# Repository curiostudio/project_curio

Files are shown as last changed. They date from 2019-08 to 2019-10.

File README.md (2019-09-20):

# An open source Human Computer Interface to help Blind users to code
 
I am working on this project for my thesis in Integrated Product Design, and I wanted to make this project open source, so as widen its
impact and ensure it reaches the last mile. As a product designer and mechanical engineer by background, I believe I am limited. This is
is an effort to explore and introduce a new approach towards bringing more blind users into the programming world. I believe, only with community development, can this project reach its fullest potential. Hence, I invite designers, engineers, computer scientists and enthusiasts to make the world of programming accessible for all. 

# The Story
I am an Integrated Product Design  student of the Industrial Design Faculty at the Delft University of Technology. My thesis is on 
'Development of a HCI device to enable blind children to learn coding'. In the 21st century, learning to code is synonymous and as 
important as learning a new language. Lack of Computational Thinking (CT), which coding helps to develop, results in blind users missing on
Lucrative jobs in the programming world. for blind people. Visually impaired people have a hard time finding job opportunities. Finding one requires their workplace
and their travel to the workplace are accessible too. On the other hand, blind people can work from home when it comes to programming jobs.
Moreover, the popular assistive tools like Refreshable Braille Displays, though inaccessible (by purchasing power) to most users,
are the 'only' available option in the market to help blind people to code. There are four major problems that prevents the majority
users in this target group to learn and use coding- 

 1) The global braille literacy is very low, meaning most of them depend on screen readers as they cannot use braille based assistive 
    aids like the Braille displays. According to the European Blind Union, braille illiteracy causes 75% of their unemployability scenarios.

 2) Refreshable braille displays are expensive, for individuals in the middle and low income groups to afford. During my research in 
    India, I found that only a  few (even) blind schools knew about these braille displays and that too they have seen only in the 
    magazines/ websites. It is simply too expensive to own one. 

 3) Screen readers (that is available for free) is designed to read only natural language and not source code. Though these softwares can be 
    configured to read symbols or to skip them, it is often difficult to say which configuration would best suited to understand the 
    code in consideration, and 

 4) Use of these aids, greatly reduces the productivity and ability collaborate (in professional environments) and ability to learn 
    from peers(in school environments)

 # Some background research

In the past two decades, several educational materials have been developed for children to learn digital skills like LEGO Mindstorms, 
BBC Micro:bit, online games and puzzles. Most programming languages for children are block based, meaning they arrange virtual blocks on
the screen to form a logical pattern. The debugging is also presented with visual cues . The output is also in the form of visual- 
animations and digital games. However these materials are not accessible to visually impaired children.  Programming languages for
children and teens are mostly block based, like SCRATCH and BLOCKLY. An Interview with the ICT teacher at a Visio, an umbrella 
organisation for blind schools  in the Netherlands,  revealed that the common medium of insruction for high school blind students 
is Python language. Studies by McKay and Kolling, 2013 explains that block languages are suited to deletion and movement, while 
textual language are suited for some other tasks like insertion and replacement. Owing to the fact that the project aims at gearing up
students to suit the employment market better, a textual programming language in python was chosen as the starting point. 

As the ICT world is becoming increasingly accessible to users with disabilities including blindness, languages like Quorum have been
developed in recent years. It is the world’s first evidence based programming language developed upon the SodBeans environment. 
Although equipped with an array of accessible features like 3D spatial sound cues, compatibility to braille devices and a well supported
team of academic developers, there comes a question if a dedicated language is welcomed by blind users. Interviews with blind programmers
have revealed that they need a more accessible language than a  dedicated programming language, mainly due to access to the unmatched 
main stream content and support (eg, P   ython, Java etc)

# Design goal
 What if an interface can be designed for blind children to learn to code (which can be also used at a professional workplace setting) 
 in order to enhance the blind user's productivity, ability to collaborate and reduce cognitive load (and hence work/study 
 related stress)? 

# Design Focus
 - Enabling blind users to skim through code (code blocks and hierarchy) and to understand the logic of the code. 
   (This is currently not possible and the users form mental mind maps to understand the code, while their sighted counterparts can   
   easily skim through code and understand it)
 - Designing a low cost, easy to build interface, so that more users in the middle and lower economic sections can benefit from the ICT 
   Job market
 - Developing an open source model, with emphasis on value generation through 'Share your wealth' business model.  

# Mentors
This project wouldn't be possible without the support and guidance of 
Dr. Ianus Keller (Interaction design teacher and thesis Chair)
Dr. Wilfred van der Vegte (Assistant Professor, Computer Aided Design Engineering and thesis Mentor) 
Mr. Richard Bekking (Electronics Expert)
Mr. Jose Calors Jurra Llanusa (Open Source Hardware Expert)

# Repository Guide
This readme provides the background information to this project. You can find all the scripts and code that run the device in the code folder, while the design files (laser cut files, 3D printing files, schematics, BOM) are in the hardware folder. The progress folder has all the information related to the progress of the project (roadmap, version map, contribution guide). The project tab shows the Kanban boards from the two development phases.

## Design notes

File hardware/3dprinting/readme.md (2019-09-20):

The internal lead screws are 3D printed in the current design. The decision to 3D print them, instead of using a standard part was to enable ease of repairability and availability of replacement lead screws (of specified pitch)

Lead Screws printing configuration:

Material: Nylon 12
Printing Method: SLS
Infill Density: 80% 
Orientation: Horizontal
Support: Touching buildplate

Travelling Nut printing configuration

Material: Nylon 12
Printing Method: SLS
Infill Density: 50%
Orientation: Vertical
Support: Everywhere

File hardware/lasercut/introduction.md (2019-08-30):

The housing of the product is designed to be DIY built, using one sheet of poplar wood and one sheet of MDF (medium density fibre). This material is chosen for its flexibility and to provide one of the curved edges for the product. 
This edge serves as the reference point for the user to know which side is up.  The joints at the moment are glued together. Future possibilities could include screws, that enhances the repairability of the product. 

Specifications: 
Sheet 1: 900 x 300 (3mm MDF)
Sheet 2: 900 x 150 (5mm Poplar wood)

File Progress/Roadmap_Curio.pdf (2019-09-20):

# Roadmap

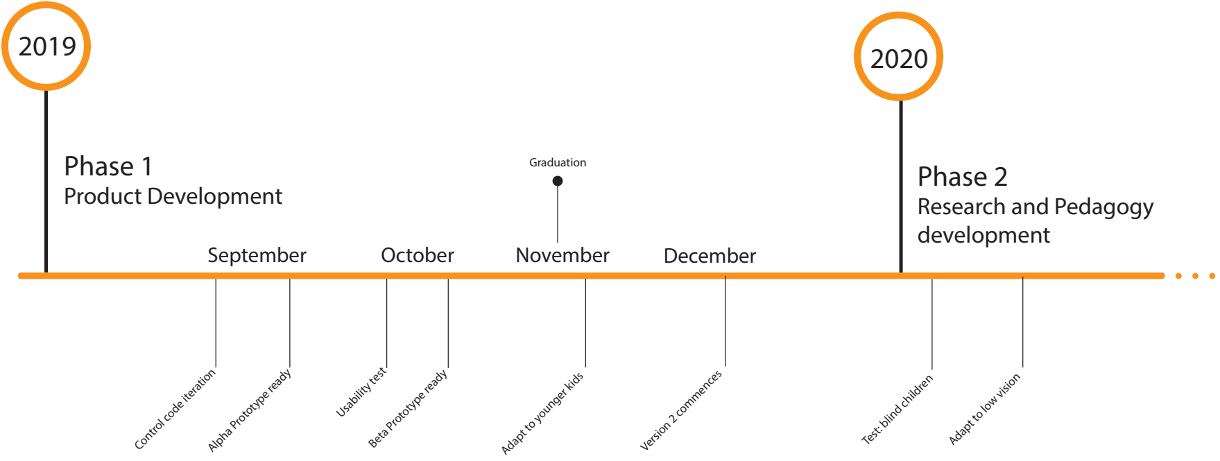
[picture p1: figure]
Alpha Prototype ready; Phase 1 Product Development; Phase 2 Research and Pedagogy; Control code iteration; Beta Prototype ready; Usability test; Version 2 commences; Graduation; Adapt to low vision; Adapt to younger kids; Test: blind children

development September | October | November | December

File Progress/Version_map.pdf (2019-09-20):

# Version Map

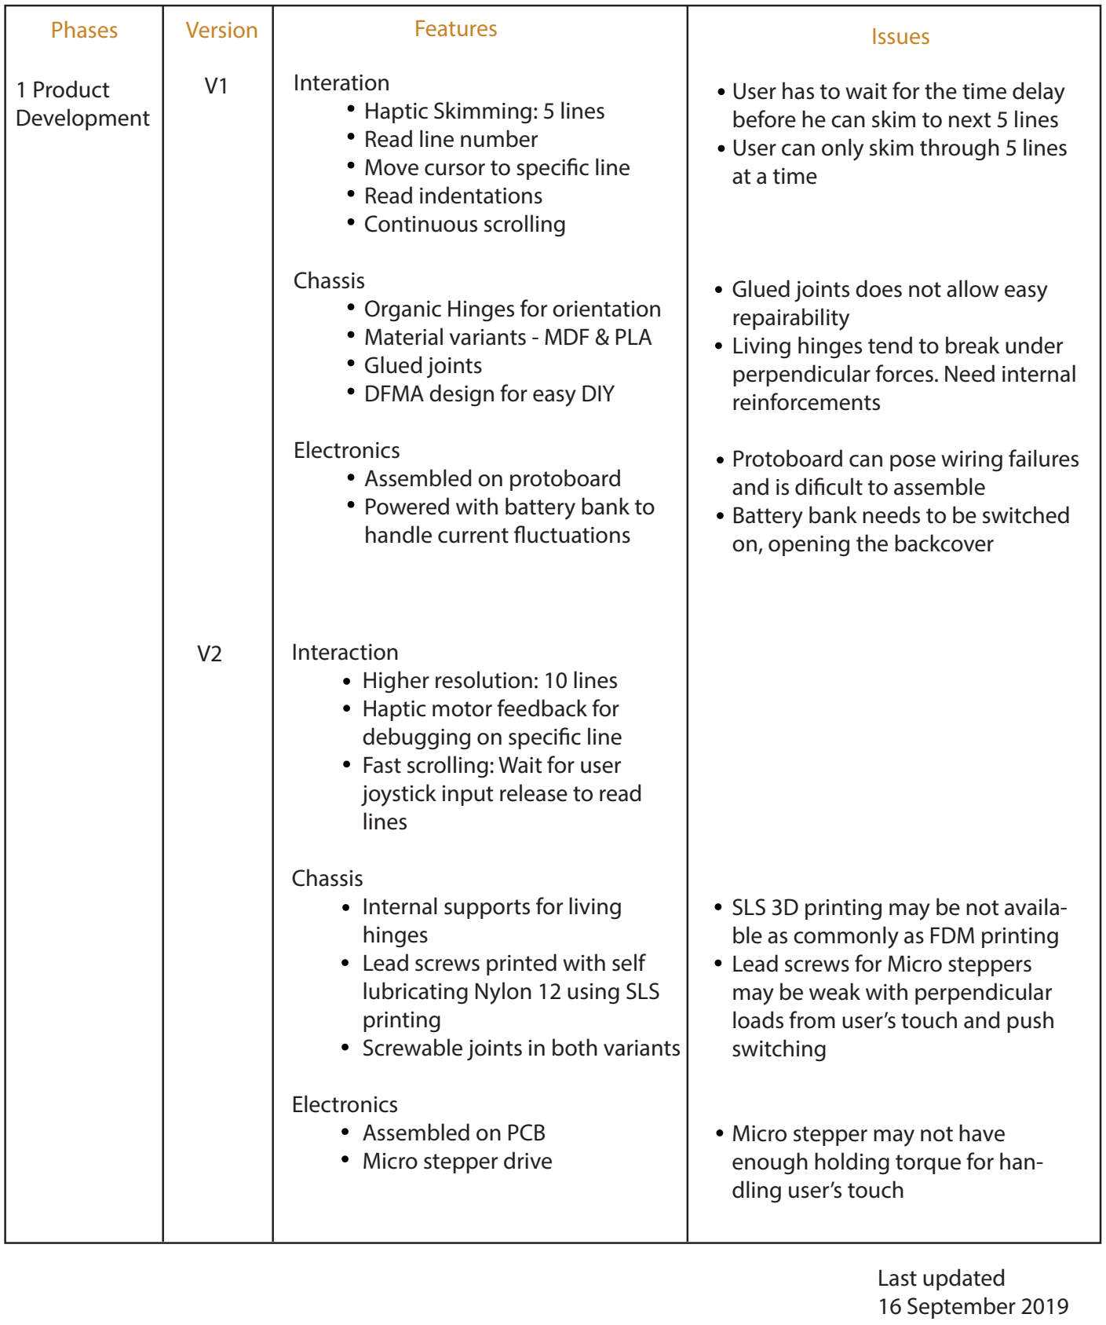
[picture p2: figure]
Phases; Version; 1 Product Development; Interation Haptic Skimming: 5 lines Read line number Move cursor to specic line Read indentations Continuous scrolling; Chassis Organic Hinges for orientation Material variants - MDF & PLA Glued joints DFMA design for easy DIY; Electronics Assembled on protoboard Powered with battery bank to handle current uctuations; Features; Interaction Higher resolution: 10 lines Haptic motor feedback for debugging on specic line Fast scrolling: Wait for user joystick input release to read lines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

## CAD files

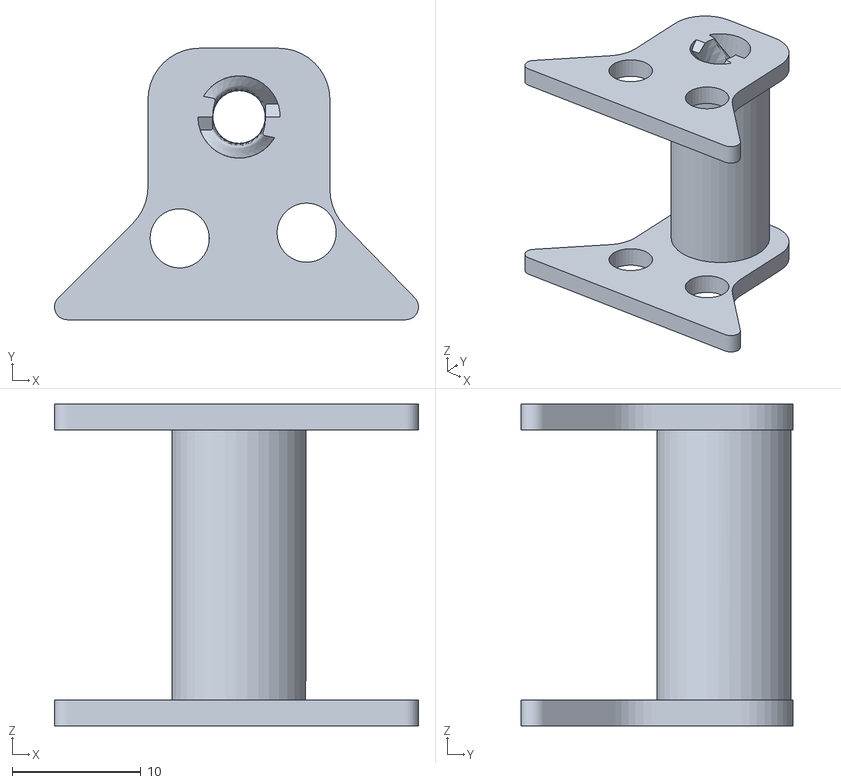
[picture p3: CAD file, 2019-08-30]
hardware/3dprinting/NUT_Joystick holder_2 start_25mm pitch.STL
28.3 x 21.1 x 25.0

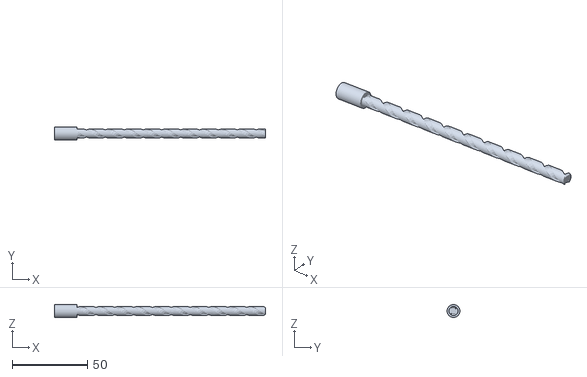
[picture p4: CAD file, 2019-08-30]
hardware/3dprinting/SCREW_125mm_Pitch35mm_cut extrude_2 START_25mm.STL
140.0 x 8.55 x 8.56

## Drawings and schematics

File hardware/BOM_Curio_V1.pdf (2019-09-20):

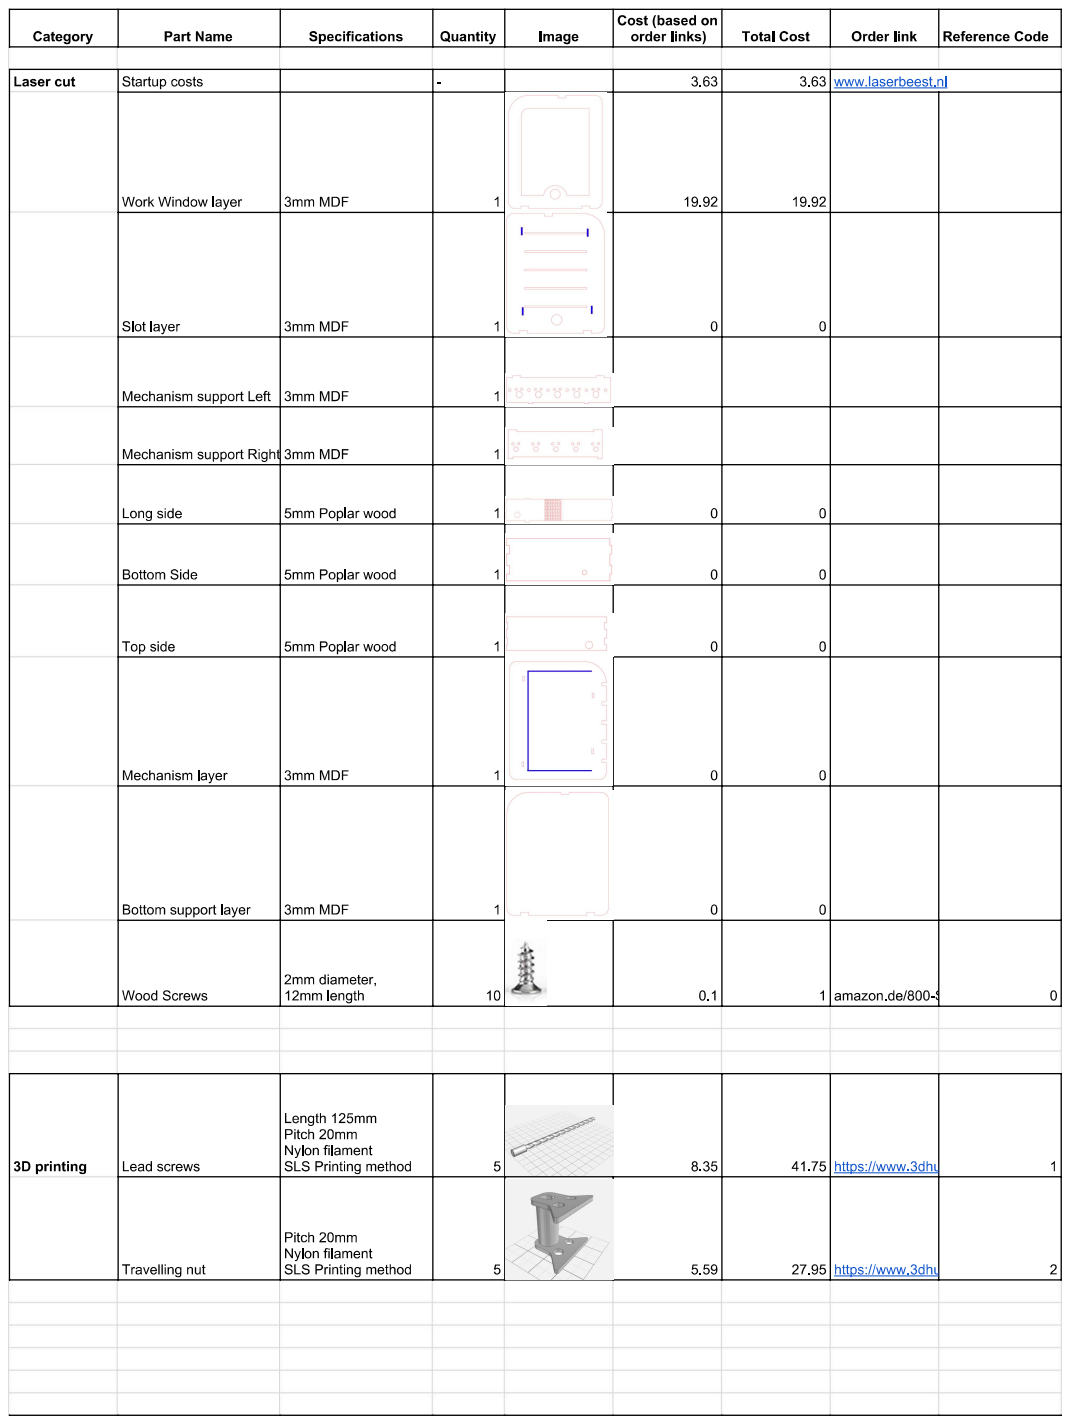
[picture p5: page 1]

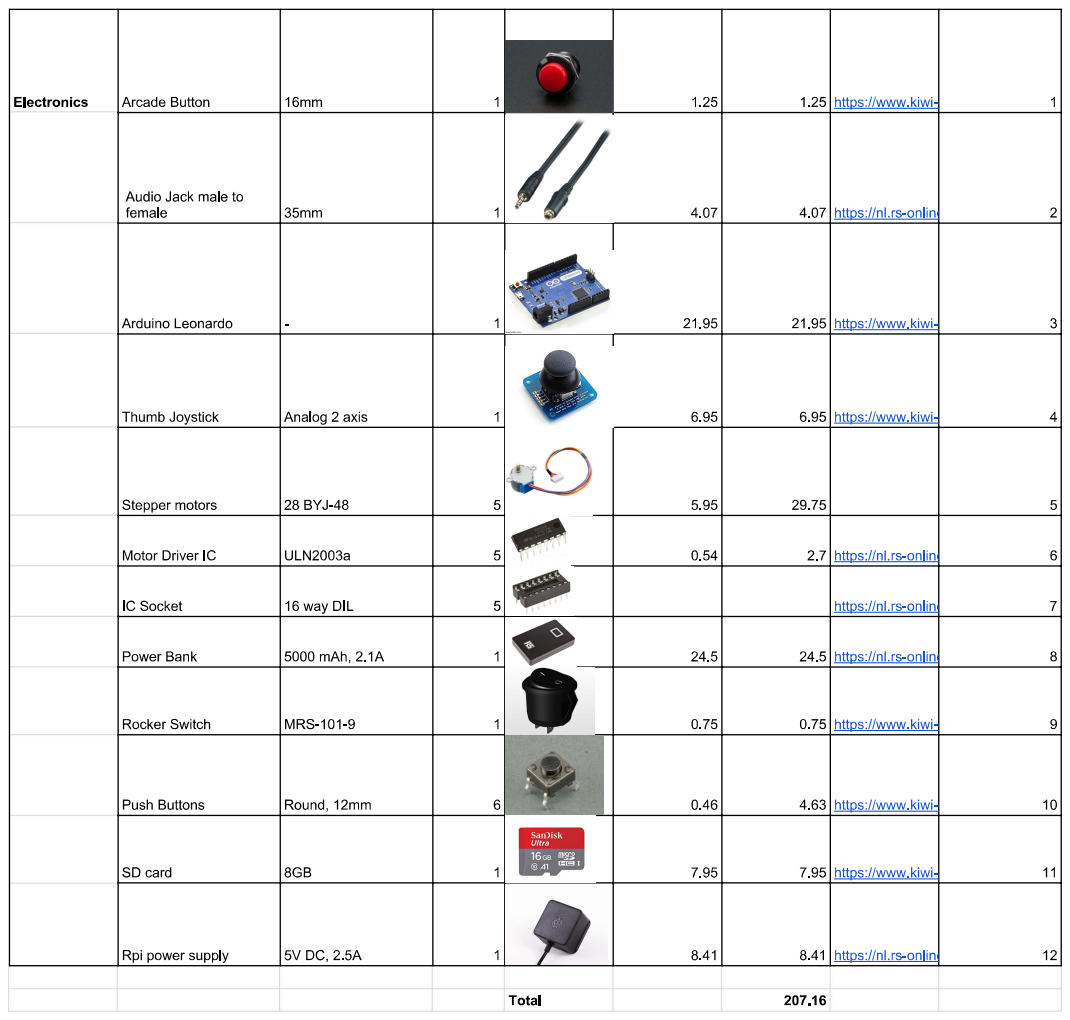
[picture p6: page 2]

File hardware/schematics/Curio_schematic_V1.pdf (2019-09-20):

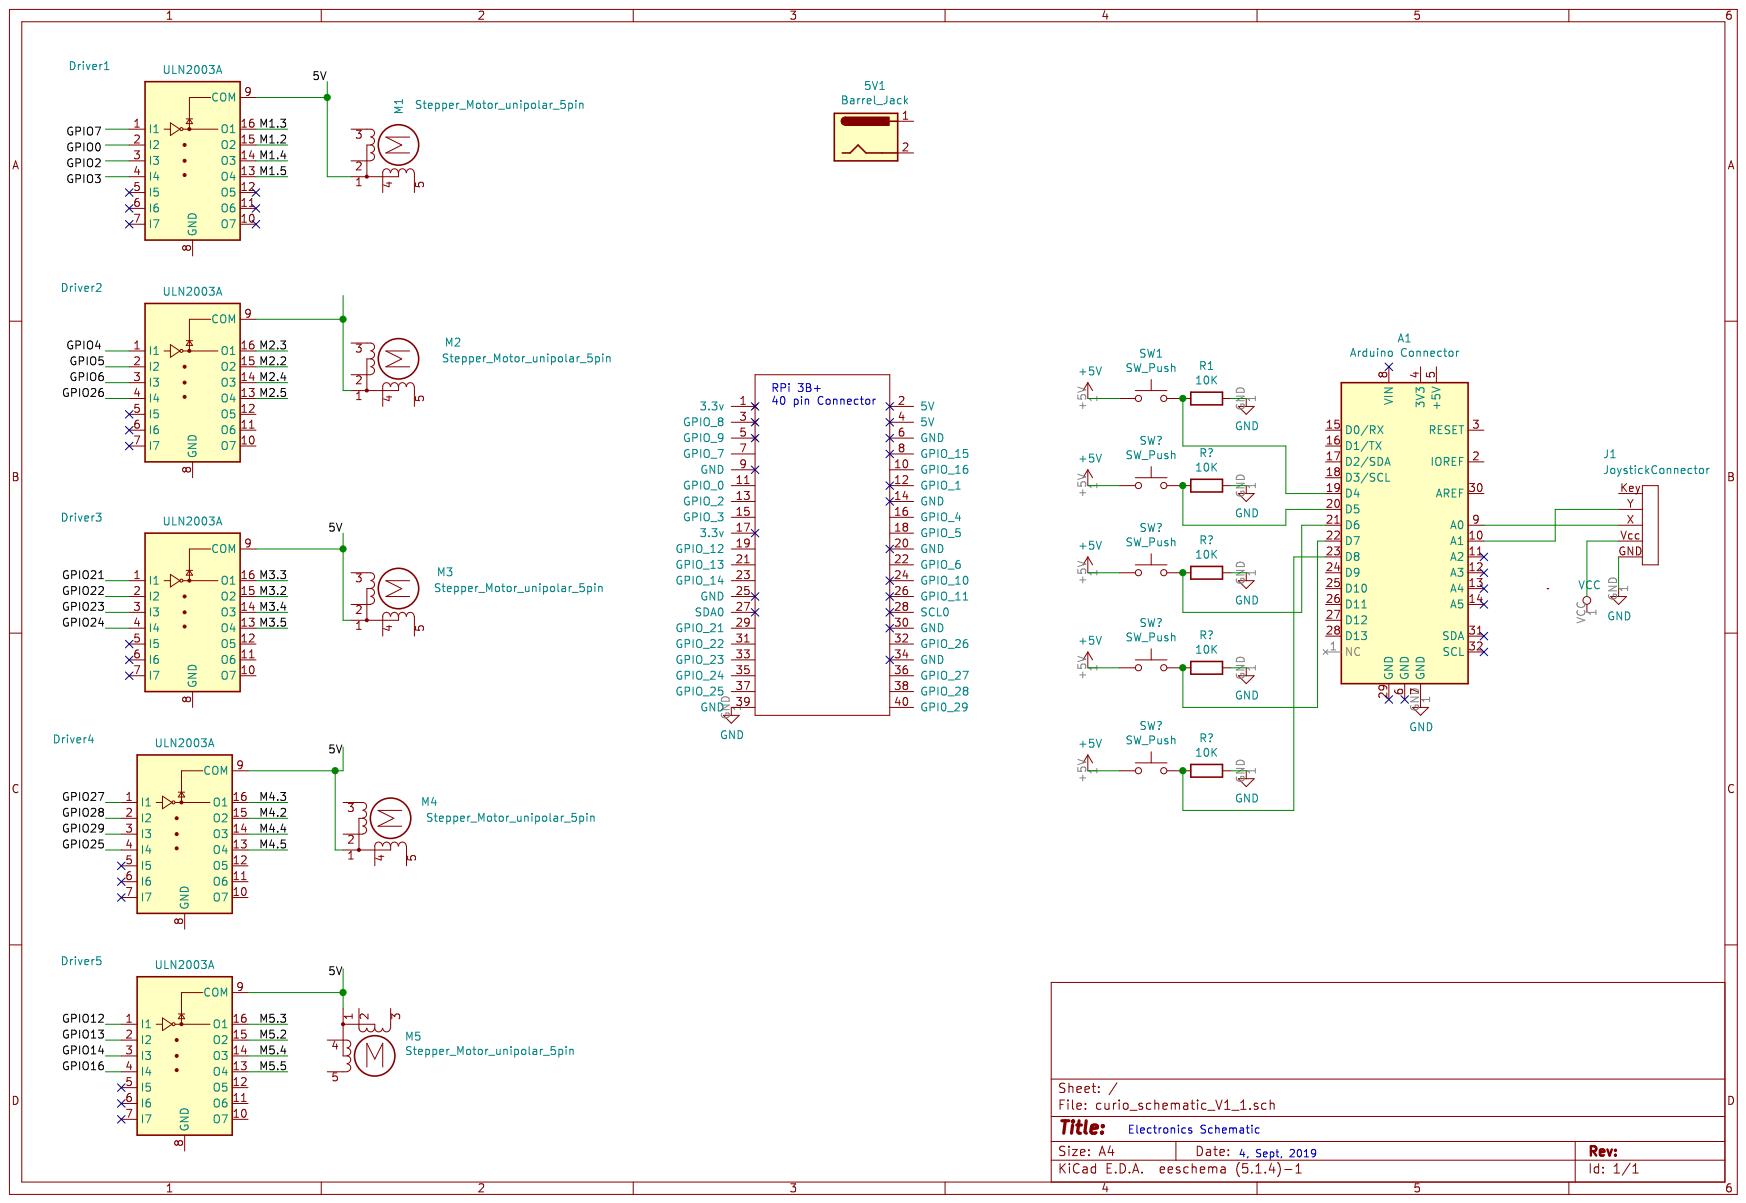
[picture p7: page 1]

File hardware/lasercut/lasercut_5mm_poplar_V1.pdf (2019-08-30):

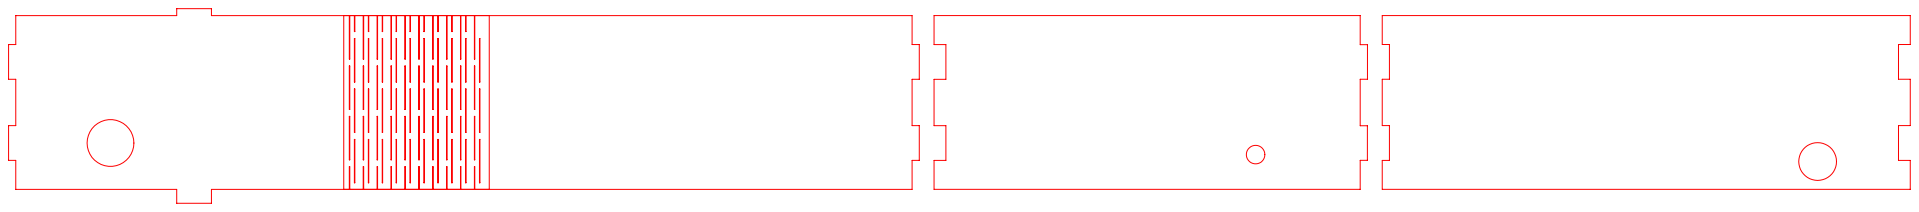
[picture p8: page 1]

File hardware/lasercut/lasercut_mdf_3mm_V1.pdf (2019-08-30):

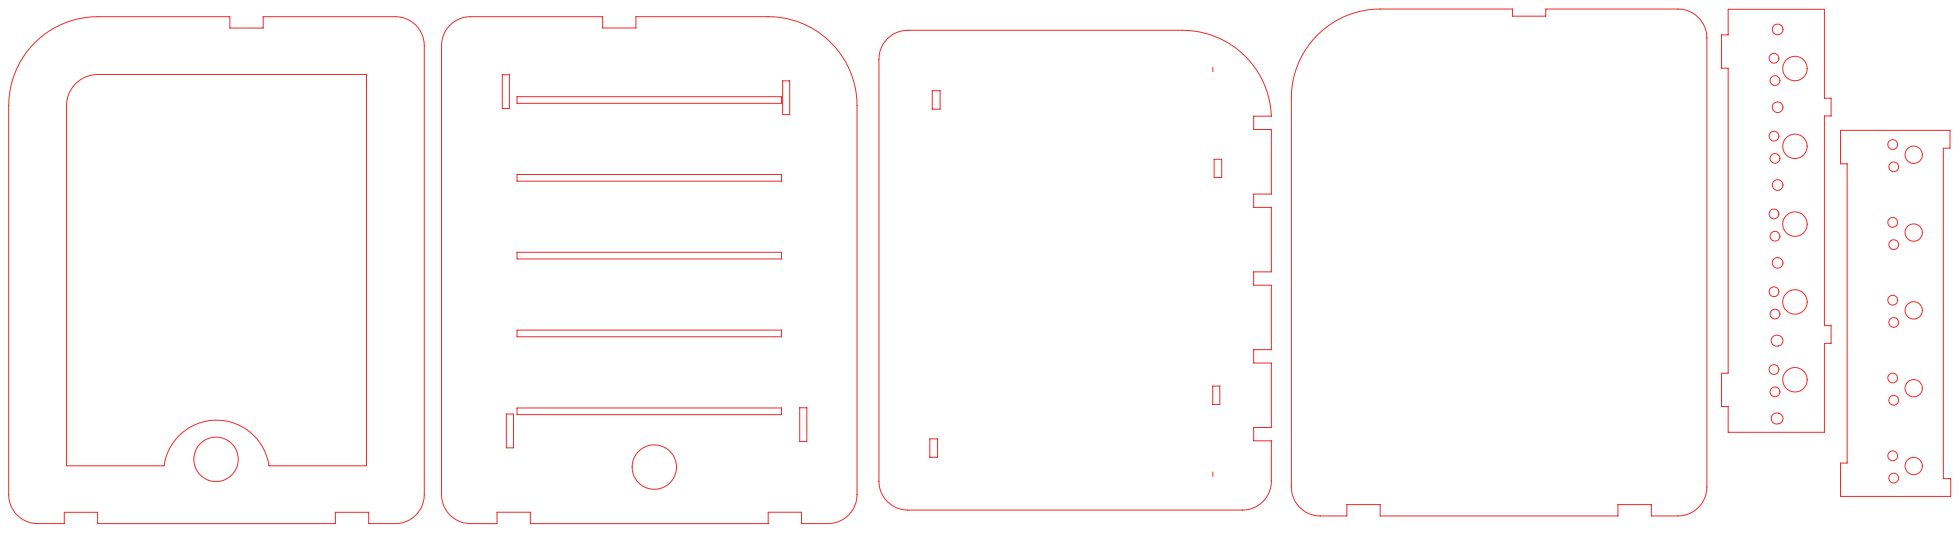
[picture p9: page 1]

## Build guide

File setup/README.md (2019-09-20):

This is a guide for the following: (to do)
- Installing collaboration design tools
- Setting up Raspberry Pi
- Using Git and its tools
- Contribution guide

# List of Software tools used

- Text editor: Atom
- Computer Aided Design (CAD): SCAD 
- Illustrations/ Laser cut files: GIMP
- 3D printing: Slic3r
- Schematics: KiCad

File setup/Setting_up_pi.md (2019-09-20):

# Setting up the Pi
Raspberry Pi acts as the CPU in this product, while arduino is a hub for all user input and communicates with the Pi. Follow the instructions below to setup the Pi and install the required scripts. 

1. Format a 8GB/16GB SD Card with FAT32 file system. You can do this either in My Computer, by right clicking the SD card drive and clicking on Format. Or, you can format using the Windows Disk Management utility

2. Download the latest Raspberry Pi OS here. I am currently using Raspbian Buster

3. Use Balena Etcher software to copy OS you just downloaded on to the SD card. Follow on-screen instructions to do so

4. Insert the SD card into the Raspberry Pi slot and power ON the Pi. Its advisable to use an external monitor (PC or Pi display) for the first time setup. If you do not have a display, you can follow this tutorial to setup the Pi

5. The on-screen instructions will guide you to setup things like country, Wi-Fi connection, keyboard layout etc. At the end of this, skip the restart request. Open the applications menu (Raspberry icon in top left of the screen) and go to preferences and then to Raspberry Pi configuration. Under the interfaces tab, enable SSH, SPI, I2C and Remote GPIO. Now restart the Pi. 

## Setting up libraries: 

For the product to run properly, you will need some libraries to be installed first. In the future versions, this could be automated with an Installer Script, so that non-technical users can install/ configure all the required steps with ease. 

1. Go to applications menu, then to Accessories and then open Terminal. 

2. Create a new folder by typing mkdir curio. Now open the newly created folder by typing cd curio. This will enable you to install all the following scrips to be installed in this folder. 

3. Install GPIO library, by typing pip install rpi.GPIO

4. Install Serial library, by typing pip install pyserial

5. Install GrovePi library, by typing 
    1.  sudo curl -kL [dexterindustries.com/update_grovepi](http://dexterindustries.com/update_grovepi) | bash 
    2. sudo pip install grovepi
    3. sudo reboot

## Getting the scripts:

Now, its time to get the script(s) to run the product. 

1. Open a new terminal, and go to the curio folder, by typing cd curio

2. Now type, nano main_program.py. A new GNU nano window opens. 

3. Copy the code from [https://github.com/curiostudio/project_curio/blob/master/code/stepper_control.py](https://github.com/curiostudio/project_curio/blob/master/code/stepper_control.py) and paste it into the nano window. Press Ctrl + x (windows) and then press Y.

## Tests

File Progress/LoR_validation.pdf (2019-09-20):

Category | Requirement | Remarks | Status

## Safety

## Reliability

## Interaction

# List of Requirements Validation

## Limited mechanical forces, so as to not to cause injury

Should not have sharp edges | Edges are sharp in the MDF version. Organic hinges failed at 10mm radius llet
Grooves should not let ngers get struck Robust in structure, assembly and operation | Slider grooves are 3mm in width, less than the width of the little nger of a 10 year old Dutch child (Dined, 1993) ‘Robustness’ was given a score of 72.5% of users while testing for Buyer’s perception of Aesthetics.
Should be based on standard computation devices | Computation based on Raspberry Pi, which was chosen for its reliable support, availability of packages and low cost (RPi Zero costs as low as 5 Euros). Input is a standard keyboard.
Tethering should be based on wired connectivity | All peripherals, internal and external are wired physically. There is no dependence on wireless connectivity.
The product should be able to bear a fall upto 4 ft | Fall test has not been yet conducted on the product. But loads on the organic hinges in the MDF variant could be the most probable breaking point.
Internal components should not be aected by temperature and dust | Dust can still enter through the slder grooves. Can be covered by a thin layer of silicone, without aecting the interaction. Could be added in the next version.
The product should have backup power | All internal electronics, including the motors are powered with a 5V 2.1A, 5000mA power bank. But it requires the user to manually power on the power bank externally. The user again has to switch on the Rocker switch to ON the RPi. Power bank model can be changed
The battery backup should last longer than 3 hours in a single charge Should be usable for six hours without signicant fatigue | There is no active power saving scheme. A NAND logic can be added later, to save power by turning o the inactive stepper motors, Ergonomically, the product is within the reach of a child, sitting on chair and using the product on a table. Productivity test to be conducted, to measure time taken before fatigue appears in arm, while reaching out to product.

## Be engaging and interactive for 12- 17 year olds

## Use tactile use cues

The holding torque is 34.3mN.m, enough for user interaction, but minimal to cause injury

‘Playful and engaging’ was given a score of 85 on Buyer’s perception of Aesthetics. Playfulness evaluation needs be conducted.

Top left corner was lled at 40mm radius to show upright orientation and workspace window indicated by a downward indentation on the top surface.
Passed | Needs improvement | Failed Updated LoR

## Production and Repairability

Category | Requirement | Remarks | Status

# List of Requirements Validation

## Wishes The product should be easy for

## The product should allow the user to collaborate with sighted/ non-sighted peers

## Setup and Use

## User should be able to easily locate specic characters or words

User should be able to skim code | Five stepper motors update button positions according to line indentation, allowing user to skim. It directly allows user to organise information he wants to listen, while creating the code logic in his mind
User should be able to use python language up to intermediate level The product should be easy to assemble by low-skilled handlers (DIY). | User can learn and use python till intermediate level (arithmetic, strings, booleans, comparison operators, loops, methods, functions) A screw driver and resin adhesive are the only tools required to assemble this product
The product should follow DFMA design principles | The design has reduced number of parts, simplied part geometry, all housing parts can be cut from two wood sheets (MDF variant) or 3D printed from the same material (PLA), self centering parts for ease of assembly and intuitve assembly logic.
The product should be able to be replicated using most commonly available technologies The product should be portable, and not weighing more than 3kg | The product uses laser cutting, SLS (or FDM, as per availability) 3D printing, to be able to manufacture the entire product. PCB can be designed and assembled on-demand by external parties. The product weighs 2.5 kg and the height can be reduced by 32.8mm in version 2 with the use of micro-stepper drive
The user should be able to setup/ pack the product in less than 5 minutes | The product can be easily packed and unpacked with the exible stand design. The startup time of the system is 1.894 s (Kernel 669ms + userspace 1.225 s)
The product should comply to the NEN safety regulations teachers to setup the product, even if he/she has little knowledge in technicalities | The NEN safety guidelines are to be reviewed yet The pyPi installation package allows non-technical users to install and update the scripts with ease

Mapping of ASCII values to a joystick, interfaced to editors like EMACSpeak and Vim allows user to read character wise or word wise, navigate to specic character or word and move the cursor there

## Interaction

Multi-modal interaction (Haptic + sound cues) with the product allows the user, to still take some time o to discuss/ collaborate with their peers. But audio feedback could be still a distraction
Passed | Needs improvement | Failed Updated LoR

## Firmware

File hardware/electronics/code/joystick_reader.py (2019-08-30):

import RPi.GPIO as GPIO
import time

GPIO.setwarnings(False)
GPIO.setmode(GPIO.BOARD)

motor_control_pins = [
    [11,  7, 15, 13], # Alice
    [16, 18, 22, 32], # Bob
    [33, 31, 29, 35], # Charlie
    [36, 37, 38, 40], # Derek
    [23, 21, 19, 10]] # Eddie

for motor in motor_control_pins:
    for pin in motor:
        GPIO.setup(pin, GPIO.OUT)
        GPIO.output(pin, 0)
  
halfstep_seq = [
  [1,0,0,0],
  [1,1,0,0],
  [0,1,0,0],
  [0,1,1,0],
  [0,0,1,0],
  [0,0,1,1],
  [0,0,0,1],
  [1,0,0,1]
]

def reverse_motor(motor):
    return [motor[2], motor[1], motor[0], motor[3]]

def set_5_indents(levels, backwards=False):
    steps_per_level = 512;
    motor_steps = [0] * 5

    for i in range(5):
        motor_steps[i] = levels[i] * steps_per_level
        
    for current_full_step in range(max(levels) * steps_per_level):
        if (not backwards):
            halfstep_range = range(8)
        else:
            halfstep_range = reversed(range(8))
            
        for halfstep in halfstep_range:
            i = 0
            for motor in motor_control_pins:
                for pin in range(4):
                    if (current_full_step < motor_steps[i]):
                        GPIO.output(motor[pin], halfstep_seq[halfstep][pin])
                i = i + 1
            
            time.sleep(0.001)

filehandle = open("indent_decode.py", 'r')
ind = []
empty = 0
j = 0
while True:
    line = filehandle.readline()
    if not line:
        break;
    elif (len(line.strip())==0):
        ind.append(empty)
        j=j+1
    else:
        leading_spaces = len(line) - len(line.lstrip())
        ind.append(leading_spaces)
        j=j+1

filehandle.close()
# ind[] ready for use

set_5_indents([2,4,2,1,0])
set_5_indents([2,4,2,1,0], True)


GPIO.cleanup()

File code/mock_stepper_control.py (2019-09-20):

# import RPi.GPIO as GPIO
import time
import os
import linecache
#import RPi.GPIO as GPIO
#GPIO.setwarnings(False)
#GPIO.setmode(GPIO.BOARD)


def static_vars(**kwargs):
    """
    Custom decorator to allow declaration of static variables like this:\n
    @static_var(variable = 0)\n
    def foo(parameters):\n
        foo.variable += 1
    """
    def decorate(func):
        for k in kwargs:
            setattr(func, k, kwargs[k])
        return func
    return decorate
# end def


def set_5_indents_real(object, levels):
    def reverse_motor(motor):
        return [motor[2], motor[1], motor[0], motor[3]]
    # end def

    steps_per_level = 512
    motor_steps = [0] * 5

    for i in range(len(levels)):
        motor_steps[i] = levels[i] * steps_per_level

    for current_full_step in range(max(levels) * steps_per_level):
        for halfstep in range(8):
            i = 0
            for motor in object.motor_control_pins:
                if (i + 1) > len(levels):
                    break

                for pin in range(4):
                    if (current_full_step < motor_steps[i]):
                        if (levels[i] < 0):
                            GPIO.output(reverse_motor(motor[0])[pin], 
                                        object.halfstep_seq[halfstep][pin])
                        elif (levels[i] > 0):
                            GPIO.output(motor[0][pin],
                                        object.halfstep_seq[halfstep][pin])
                i = i + 1

            time.sleep(0.001)
# end def


def set_5_indents_mock(object, levels):
    print("mock code")
    steps_per_level = 1
    motor_steps = [0] * 5

    for i in range(len(levels)):
        motor_steps[i] = levels[i] * steps_per_level

    for current_full_step in range(max(levels) * steps_per_level):
        i = 0  # Keeps track of the motor indices
        for motor in object.motor_control_pins:
            if (i + 1) > len(levels):
                break
            # end if

            if current_full_step < abs(motor_steps[i]):
                if levels[i] > 0:
                    print(f"Forward: {motor[1]}")
                elif levels[i] < 0:
                    print(f"Reverse: {motor[1]}")
                else:
                    pass  # The else-clause should never be visited
                # end if
            # end if
            i = i + 1
        # end for
# end def


class indent_decoder:
    def load_file(self, filename):
        """
        Load all indent information from the file and returns a list of
        indentations
        """

        print(f"[indent_decoder] Opening file: {filename}.")

        with open(filename, 'r') as f:
            content = f.readlines()

        self.indentations = [(len(line) - len(line.lstrip())) >> 2 for line in content]

        print(f"[indent_decoder] Loaded {len(self.indentations)} lines.")

    # end def


    def get_values(self, start_line, num=5):
        " Returns five lines from the input buffer "
        return self.indentations[start_line:start_line+num]
    # end def

    def get_total_lines(self):
        return len(self.indentations)
    # end def
# end class


class stepper_control:
    def __init__(self):
        self.motor_control_pins = [
            ([11,  7, 15, 13], "Alice"),
            ([16, 18, 22, 32], "Bob"),
            ([33, 31, 29, 35], "Charlie"),
            ([36, 37, 38, 40], "Derek"),
            ([23, 21, 19, 10], "Eddie")]
        
        self.halfstep_seq = [
            [1, 0, 0, 0],
            [1, 1, 0, 0],
            [0, 1, 0, 0],
            [0, 1, 1, 0],
            [0, 0, 1, 0],
            [0, 0, 1, 1],
            [0, 0, 0, 1],
            [1, 0, 0, 1]]
        return
    # end if


    def set_indents(self, levels):
        set_5_indents_mock(self, levels)
        return
    # end if
# end class


class curio:
    def __init__(self):
        self.active_line = 0
        self.speech_line = 0
        self.display_lines = 5
        return
    # end def


    def next_page(self):
        self.active_line = self.active_line + 5
        self.speech_line = 1
        self.display_lines = 5
        return
    # end def


    def previous_page(self):
        self.active_line = self.active_line - 5
        self.speech_line = 1
        self.display_lines = 5
        return
    # end def

    def get_line_from_file(self, linenumber):
        return []
    # end def

    def run(self):
        pass
    # end def
# end class


curio_app = curio()
indents = indent_decoder()
indents.load_file("mock_stepper_control.py")
steppers = stepper_control()
active_line = 0
display_lines = 5
userinput = ""


@static_vars(page=[0] * 5)
@static_vars(previous_page=[0] * 5)
def update_interface(start_line, visible_lines):
    " Calculates the new state of the interface "
    print(f"Showing lines: {start_line + 1} - {start_line + visible_lines}")
    update_interface.page = indents.get_values(active_line)

    print("prev\tnext\t|\tdifference")
    levels = []
    for p1, p2 in zip(update_interface.previous_page, update_interface.page):
        print(p1, p2, "|", p2 - p1, sep="\t")
        levels.append(p2 - p1)

    steppers.set_indents(levels)

    update_interface.previous_page = update_interface.page
# end def


if indents.get_total_lines() <= 5:
    update_interface(0, indents.get_total_lines())
    print(f"Showing lines: 1 - {indents.get_total_lines()}")
else:
    while True:

        curio_app.run()

        # User selected Next page
        if (userinput == "n") and ((active_line + 5) <= indents.get_total_lines()):
            active_line = active_line + 5
            speech_line = 1
            display_lines = 5

        # User selected Previous page
        elif (userinput == "p") and ((active_line - 5) >= 0):
            active_line = active_line - 5
            speech_line = 1
            display_lines = 5

        # User selected Quit program
        elif userinput == "q":
            break

        elif userinput.isdigit():
            if (int(userinput) > 0) and (int(userinput) <= 5):
                speech_line = active_line + int(userinput)
                print(f"Active line: {int(userinput)}\n")
            else:
                print("Number not in range [1-5]\n")

        elif userinput.isalpha():
            if (userinput >= "A") and (userinput <= "Z"):
                word_number = ord(userinput[0]) - ord("A")
                print(f"word# {word_number}")
                #  `print(fetch_word(filename, speech_line, word_number))
            else:
                print("Letter not in range [A-Z]\n")

        # User entered invalid character
        else:
            pass

        if active_line + display_lines > indents.get_total_lines():
            display_lines = indents.get_total_lines() - active_line

        update_interface(active_line, display_lines)
        userinput = input("(N)ext | (P)revious | Relative line#[1-5] | Word# in line[A-Z] | (Q)uit > ")
    # end while

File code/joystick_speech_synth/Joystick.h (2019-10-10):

#ifndef JOYSTICK_H_
#define JOYSTICK_H_

#include <Arduino.h>

template <typename T> 
struct lmh_t {
  T low;
  T mid;
  T high;  
};

// This three-point map function overloads the existing two-point map function
template <typename T> 
T map(T in, lmh_t<T> from, lmh_t<T> to)
{
  T mapped_val;
  
  if (in < from.mid) {
    mapped_val = map(in, from.low, from.mid, to.low, to.mid);
  }
  else {
    mapped_val = map(in, from.mid, from.high, to.mid, to.high);
  }
  
  return mapped_val;  
}

class Joystick
{
  public:

    Joystick(int pin_x, int pin_y);
    int16_t getX() const;
    int16_t getY() const;
    bool isPressed() const;

    void calibrate();
    void process();

  private:

    static constexpr int16_t X_PRESSED_VALUE = 1023;
    static constexpr int16_t LOW_COORD_VALUE = -512;
    static constexpr int16_t HIGH_COORD_VALUE = 512;

    int pin_x_ = 0;
    int pin_y_ = 0;

    lmh_t<int16_t> x_limits_{HIGH_COORD_VALUE, LOW_COORD_VALUE, 0};
    lmh_t<int16_t> y_limits_{HIGH_COORD_VALUE, LOW_COORD_VALUE, 0};
    int16_t x_ = 0;
    int16_t y_ = 0;
    int16_t raw_x_ = 0;
    int16_t raw_y_ = 0;
    bool    pressed_ = false;
};

#endif // JOYSTICK_H_

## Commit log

2019-08-30 Specifications of laser cut
2019-08-30 3D printing introduction
2019-08-30 Add files via upload
    Nuts and Screws to be printed with PLA 80% infill. Post processing is required (sanding with P80, P240 followed by spraying with PTFE lubricant)
    [NUT_Joystick holder_2 start_25mm pitch.STL, SCREW_125mm_Pitch35mm_cut extrude_2 START_25mm.STL]
2019-08-31 Added mock code to test without an actual raspi. Next feature: implement function to return the difference between two stepper configurations so we can efficiently update the interface
2019-09-01 Added user interface to the stepper_control.py files
    Next thing to do is to implement all the new features into this file.
    But I need to physically present to test the steppers.
2019-09-01 Wired update_interface into the appropriate places in the code
2019-09-19 Assembly walkthrough added
2019-10-10 Stepper test code added
